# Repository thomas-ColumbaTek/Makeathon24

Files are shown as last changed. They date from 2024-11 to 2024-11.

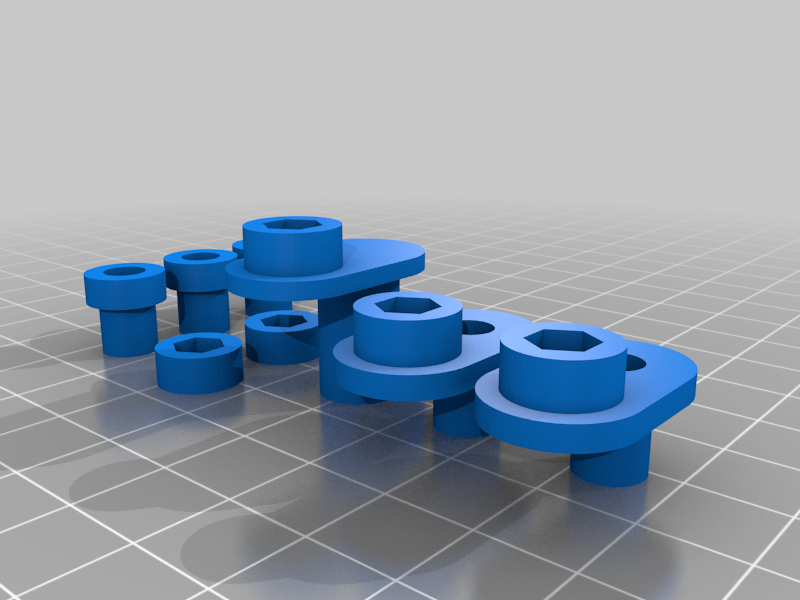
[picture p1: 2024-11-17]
OrbitalShaker/images/835a03b251431fa01c48ba5c81ab6af8.png

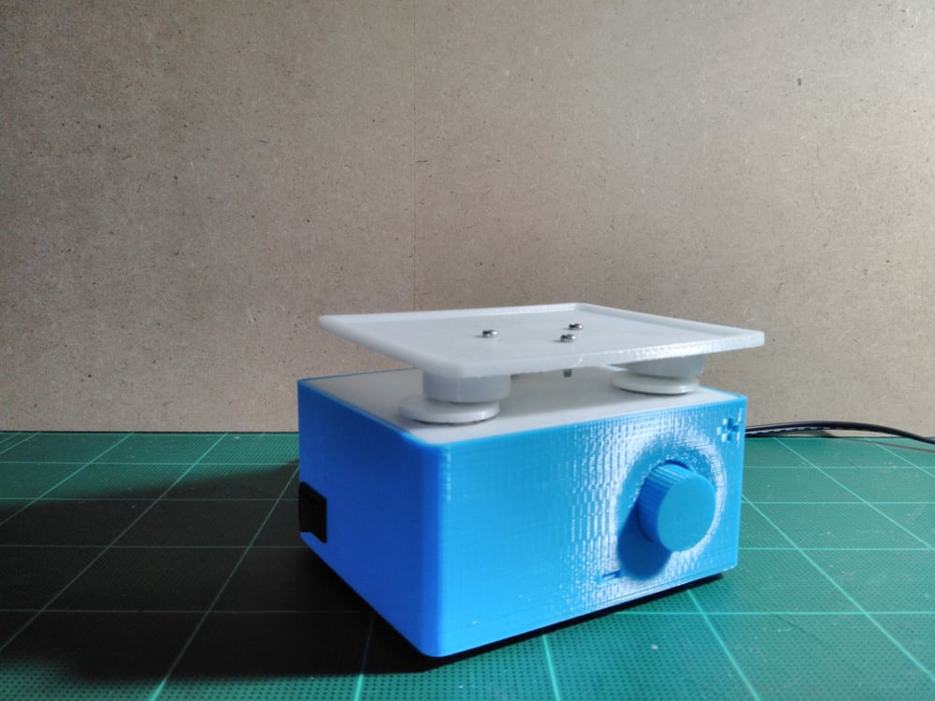
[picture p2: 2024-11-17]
OrbitalShaker/images/IMG_20171108_205839.jpg

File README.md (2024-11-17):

## Welcome to Makeathon2024 Repo

## Orbital Shaker
based on the awesome work:

DIYbio Orbital Shaker V 1.0  by ProgressTH on Thingiverse: https://www.thingiverse.com/thing:2633507

#License
CC BY
DIYbio Orbital Shaker V 1.0
by ProgressTH is licensed under the Creative Commons - Attribution license.

# DIYbio Orbital Shaker V 1.1

Changes:
	- Recreated Linages for usage with heated inserts instead of glued nuts
	- Recreated "Potitower" for better fit and screwed connection to poti and optinal usage of heated inserts
	- Recreated Platform Support with embedded Bearings and inserts
	- Created a Print file for whole Project 
	
## Syringe Pump
based on the awesome work:
Open-Source Syringe Pump by AndreySamokhin - Thingiverse

#License
License CC BY-SA

Open-Source Syringe Pump by AndreySamokhin on Thingiverse: https://www.thingiverse.com/thing:4194094
by AndreySamokhin is licensed under the Creative Commons - Attribution - Share Alike license.

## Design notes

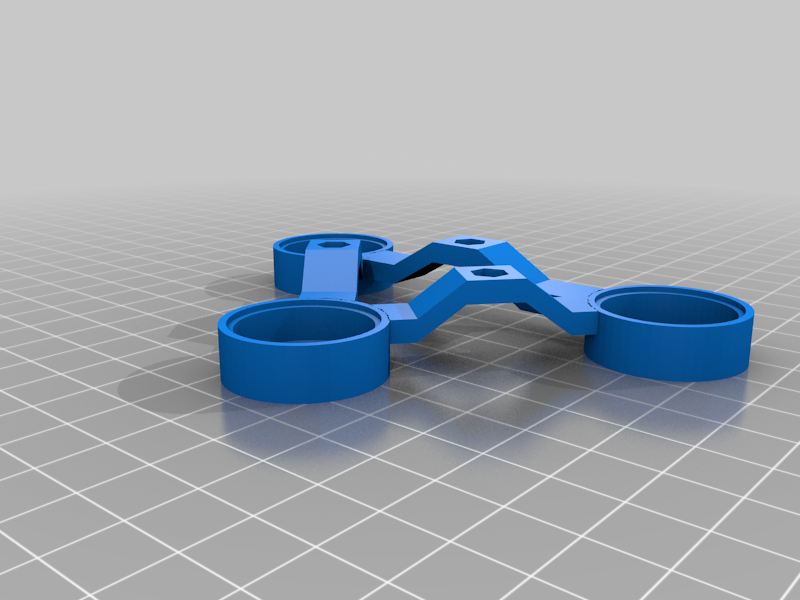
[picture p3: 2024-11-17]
OrbitalShaker/images/801bc46a1355028e08165fc7dd076f1f.png

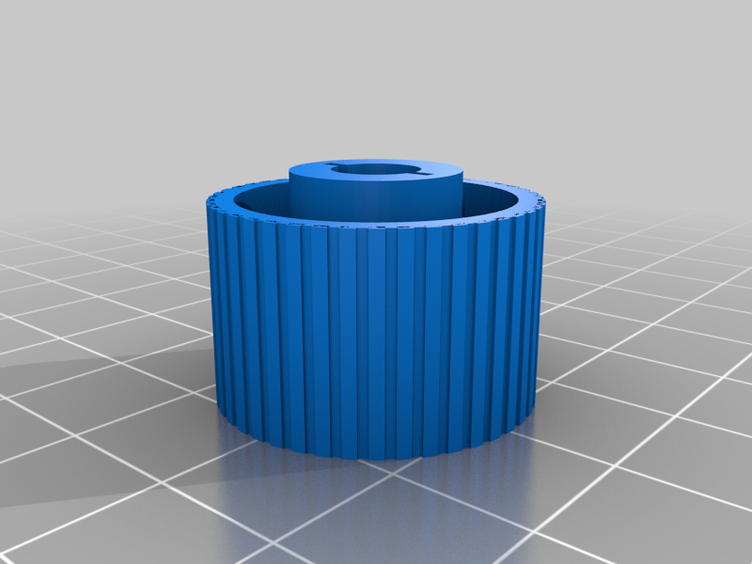
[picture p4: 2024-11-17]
OrbitalShaker/images/b9155d2c6746c89c5fc035d0d0019a35.png

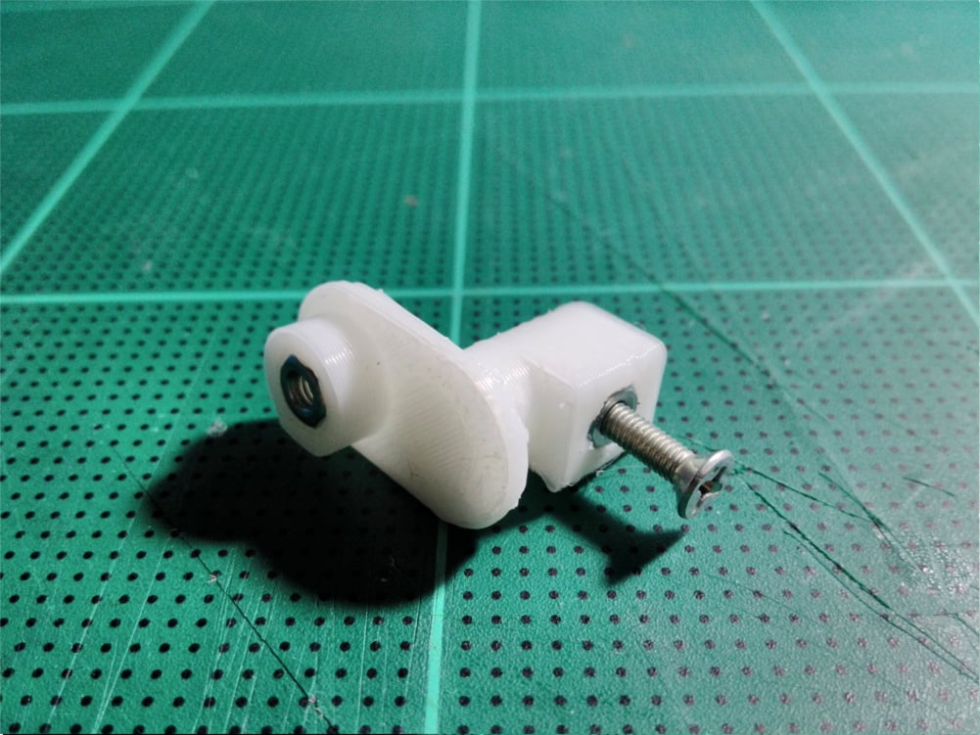
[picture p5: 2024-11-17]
OrbitalShaker/images/StepperCoupling.jpg

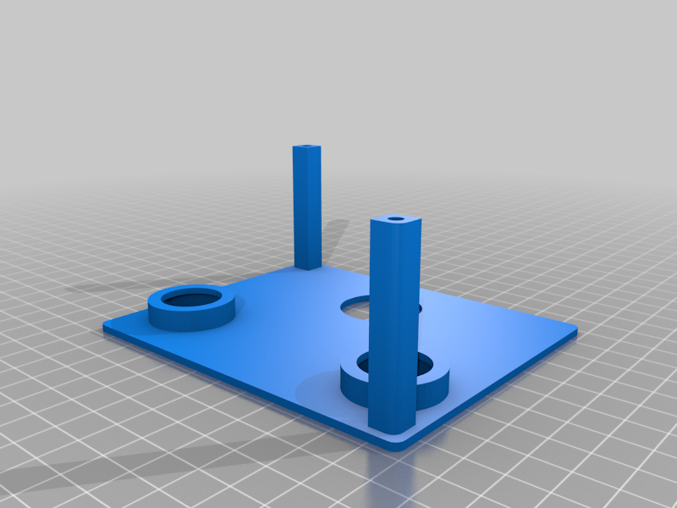
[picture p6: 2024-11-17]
OrbitalShaker/images/b79b12a18a87436c865f9c8a0832d261.png

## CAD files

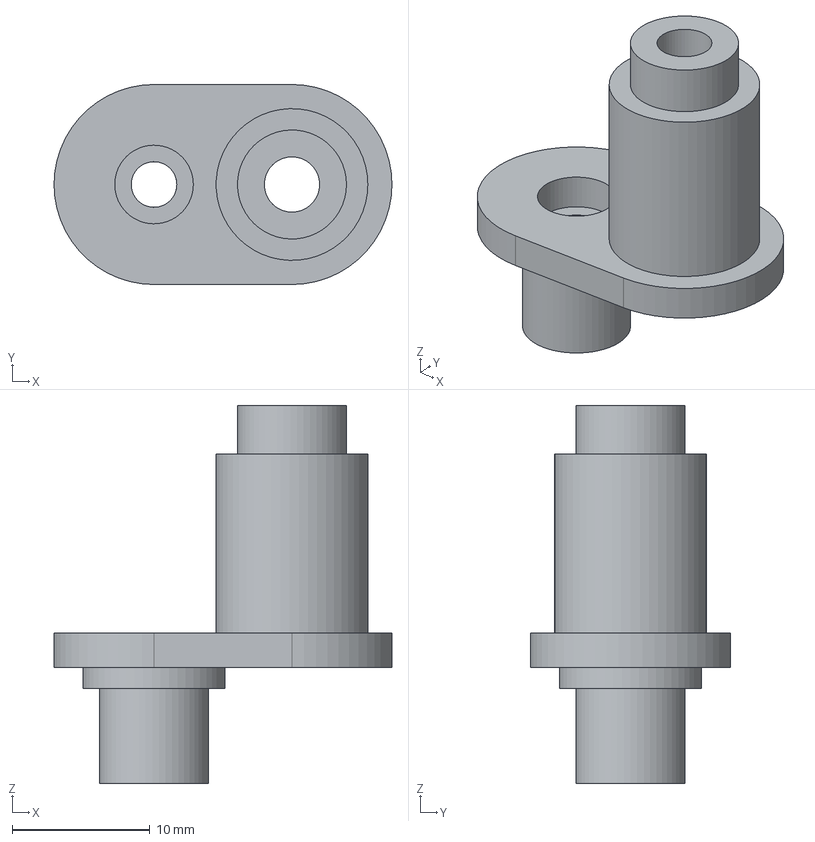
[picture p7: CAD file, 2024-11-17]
OrbitalShaker/Mechanics/linkage-linkage.step
24.5 x 14.5 x 27.4 mm

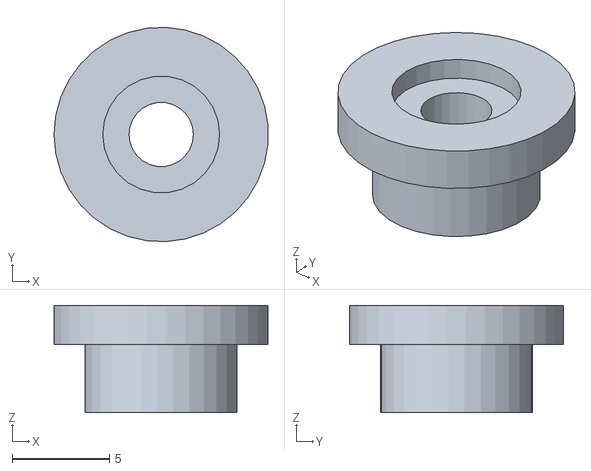
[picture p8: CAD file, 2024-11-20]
OrbitalShaker_Maya_Workshop/insert-insert.obj
11.0 x 11.0 x 5.50

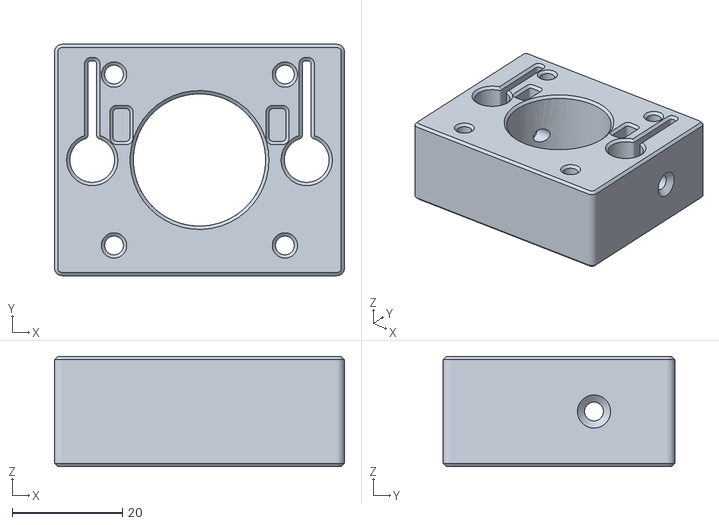
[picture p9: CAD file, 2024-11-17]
SyringePump/Mechanics/backSupport.stl
52.6 x 42.0 x 20.0

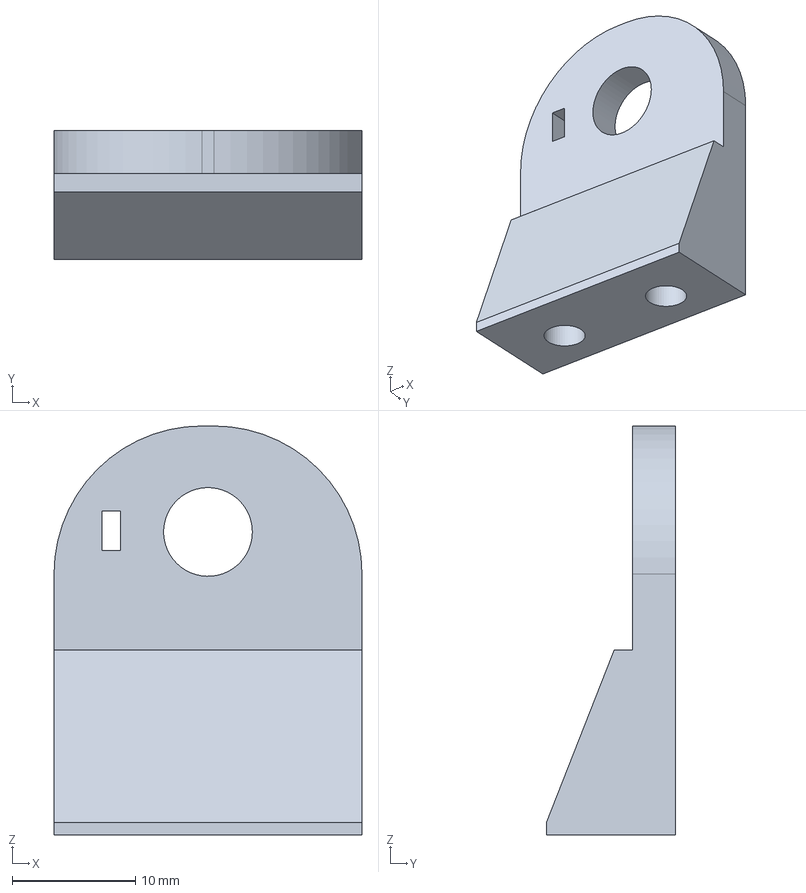
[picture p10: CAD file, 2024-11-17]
OrbitalShaker/Mechanics/PotiTower.FCStd
25.0 x 10.5 x 33.2 mm

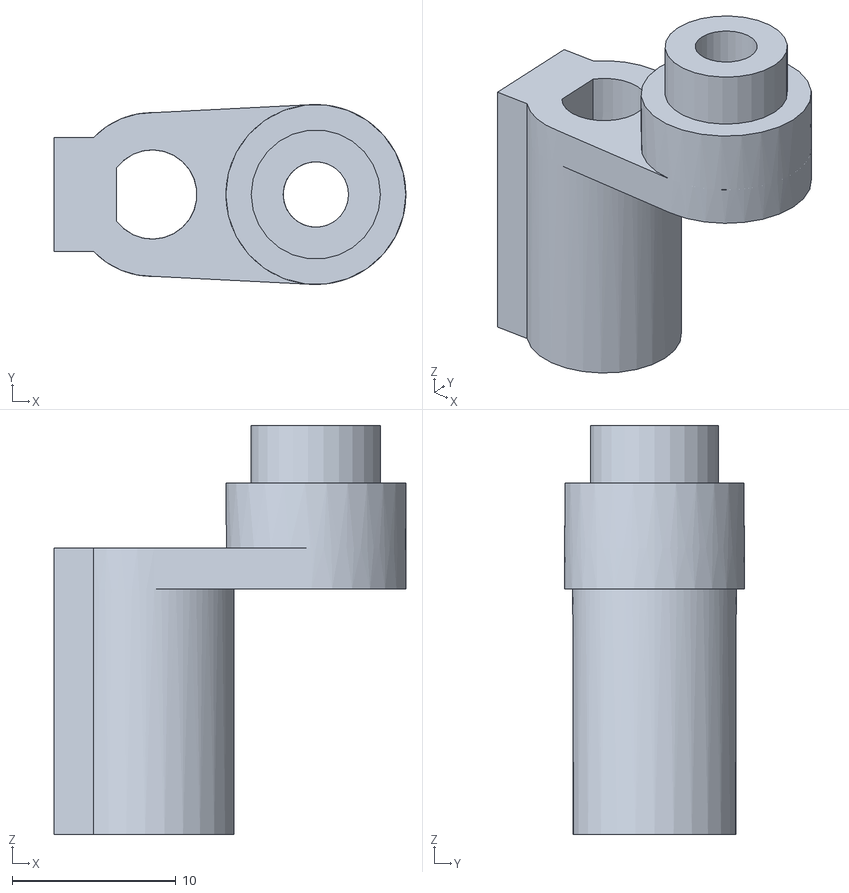
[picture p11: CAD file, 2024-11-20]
OrbitalShaker_Maya_Workshop/linkage2-linkage2.obj
21.5 x 11.0 x 25.0

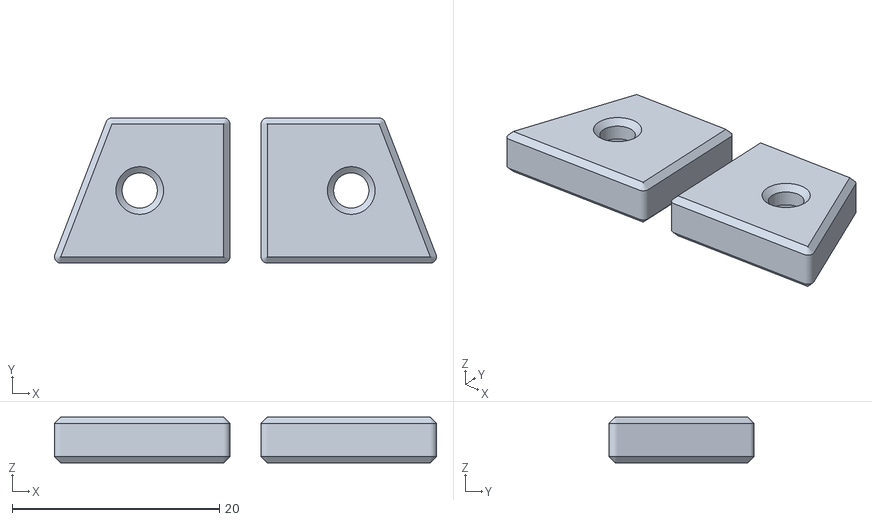
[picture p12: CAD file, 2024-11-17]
SyringePump/Mechanics/plungerHolders.stl
36.8 x 14.0 x 4.40

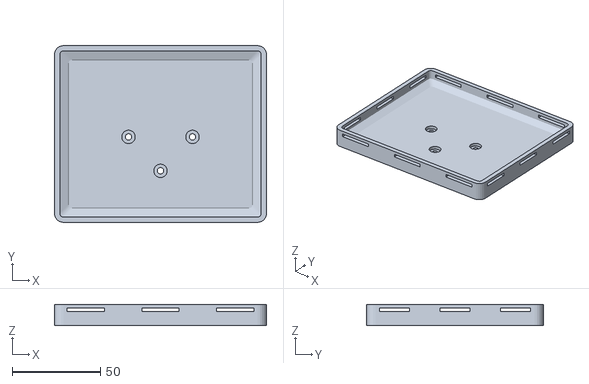
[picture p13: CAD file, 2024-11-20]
OrbitalShaker_Maya_Workshop/Unbenannt3-NewPlatform.obj
120.0 x 100.0 x 12.0

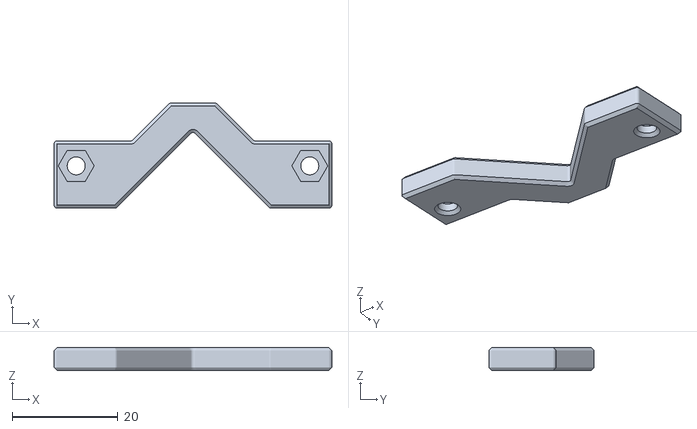
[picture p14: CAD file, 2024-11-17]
SyringePump/Mechanics/sideSyringeHolder.stl
52.6 x 19.9 x 4.40

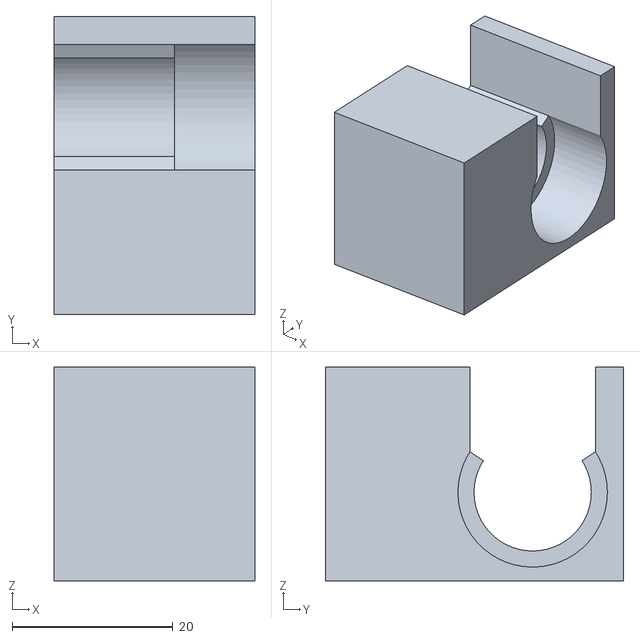
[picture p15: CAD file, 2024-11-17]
OrbitalShaker/Mechanics/Shaker_Potentiometer.stl
25.0 x 37.1 x 26.6

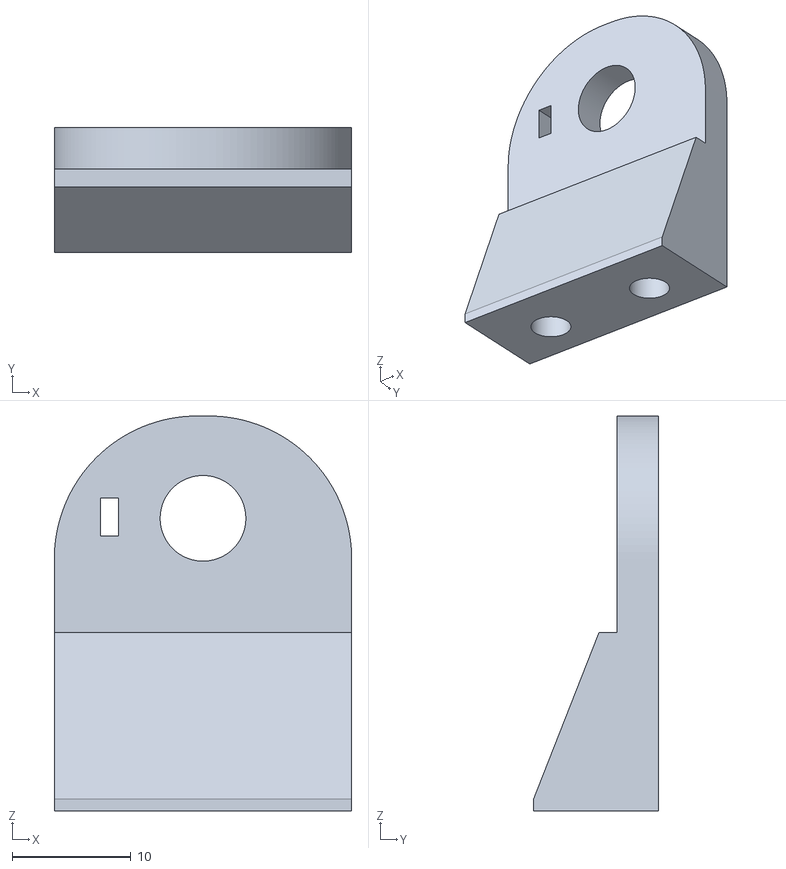
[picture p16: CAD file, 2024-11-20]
OrbitalShaker_Maya_Workshop/PotiTower-Körper.obj
25.0 x 10.5 x 33.2

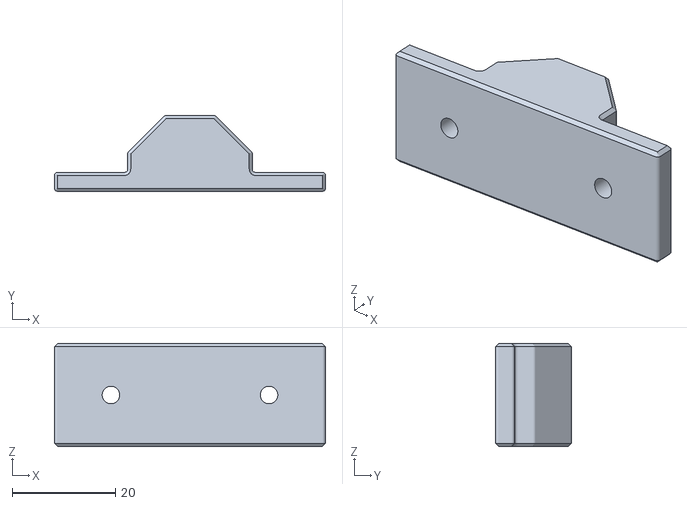
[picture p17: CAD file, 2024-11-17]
SyringePump/Mechanics/topSyringeHolder12mm.stl
52.6 x 14.7 x 20.0

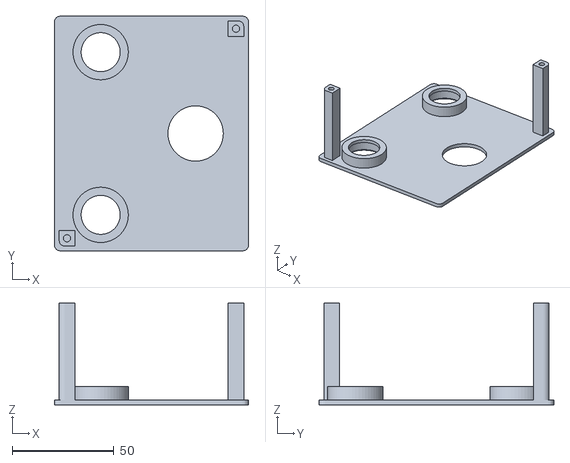
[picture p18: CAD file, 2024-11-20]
OrbitalShaker_Maya_Workshop/Unbenannt1-Shaker_CaseTop.obj
95.4 x 115.4 x 50.0

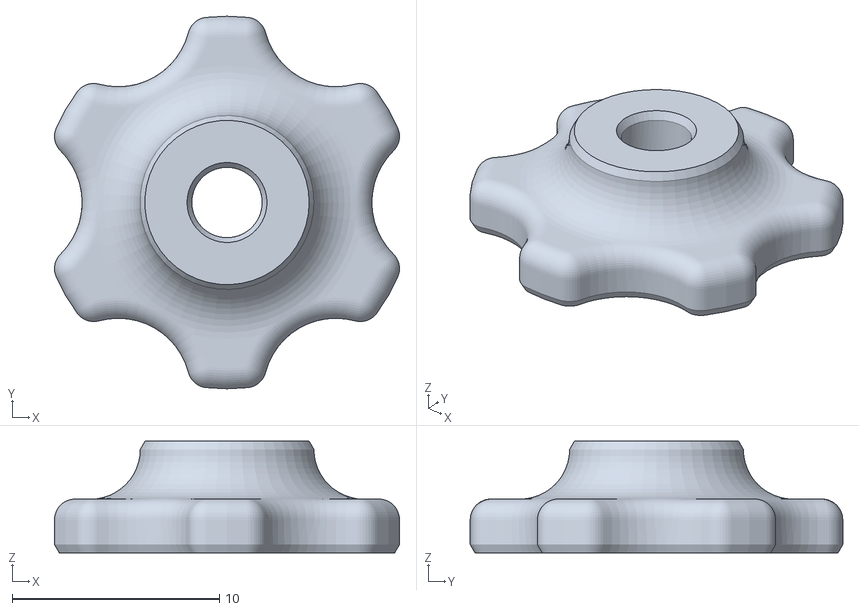
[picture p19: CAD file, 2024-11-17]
SyringePump/Mechanics/handKnob9mm.stl
16.7 x 18.0 x 5.40

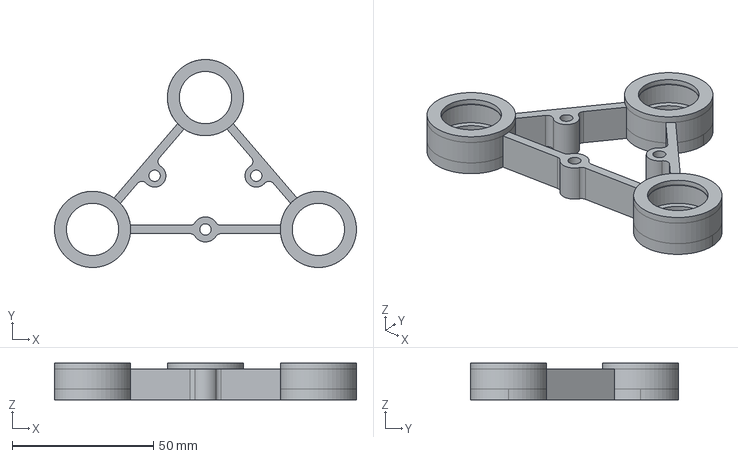
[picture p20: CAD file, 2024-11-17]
OrbitalShaker/Mechanics/PlatformSupport_NEW-support platform.step
107.0 x 73.7 x 13.0 mm

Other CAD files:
OrbitalShaker/Mechanics/linkage2-linkage2.step
OrbitalShaker/Mechanics/insert-insert.step
OrbitalShaker_Maya_Workshop/Shaker_Case.obj
SyringePump/Mechanics/carriage_lm8uu.stl
OrbitalShaker/Mechanics/ControllerPiggyback-Körper001.3mf
OrbitalShaker/Mechanics/ControllerPiggyback.FCStd
OrbitalShaker/Mechanics/OrbitalShaker_all.3mf
OrbitalShaker/Mechanics/PlatformSupport_NEW.FCStd
OrbitalShaker/Mechanics/PotiTower-Körper.3mf
OrbitalShaker/Mechanics/Seeed Studio XIAO-ESP32-C3.step
OrbitalShaker/Mechanics/Shaker.skp
OrbitalShaker/Mechanics/Shaker_Case.stl
OrbitalShaker/Mechanics/Shaker_CaseTop.stl
OrbitalShaker/Mechanics/Shaker_Feet.stl
OrbitalShaker/Mechanics/Shaker_Knob.stl
OrbitalShaker/Mechanics/Shaker_Platform.stl
OrbitalShaker/Mechanics/Washer-washer.step
OrbitalShaker/Mechanics/Washer.FCStd
OrbitalShaker/Mechanics/insert.FCStd
OrbitalShaker/Mechanics/linkage.FCStd
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

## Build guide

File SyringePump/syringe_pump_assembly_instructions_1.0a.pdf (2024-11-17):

# Open-Source Syringe Pump

(developed by Andrey Samokhin in 2018)

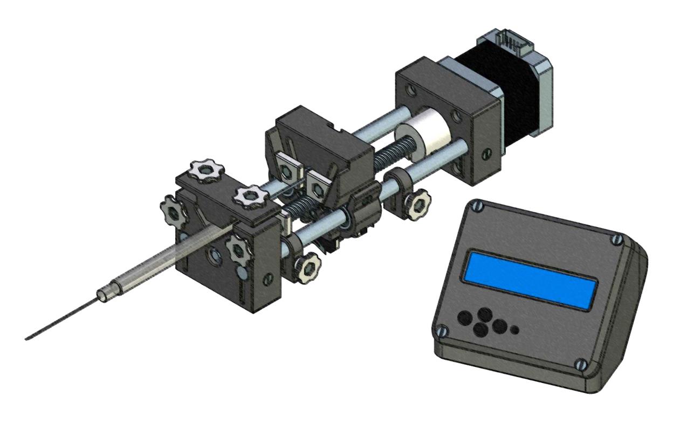
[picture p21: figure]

# Assembly Instructions

(Version 1.0a)

STL-files and "firmware" are available at http://www.mass-spec.ru/projects/diy/syringe_pump/eng/
Project files are distributed under CC BY-SA 4.0 license

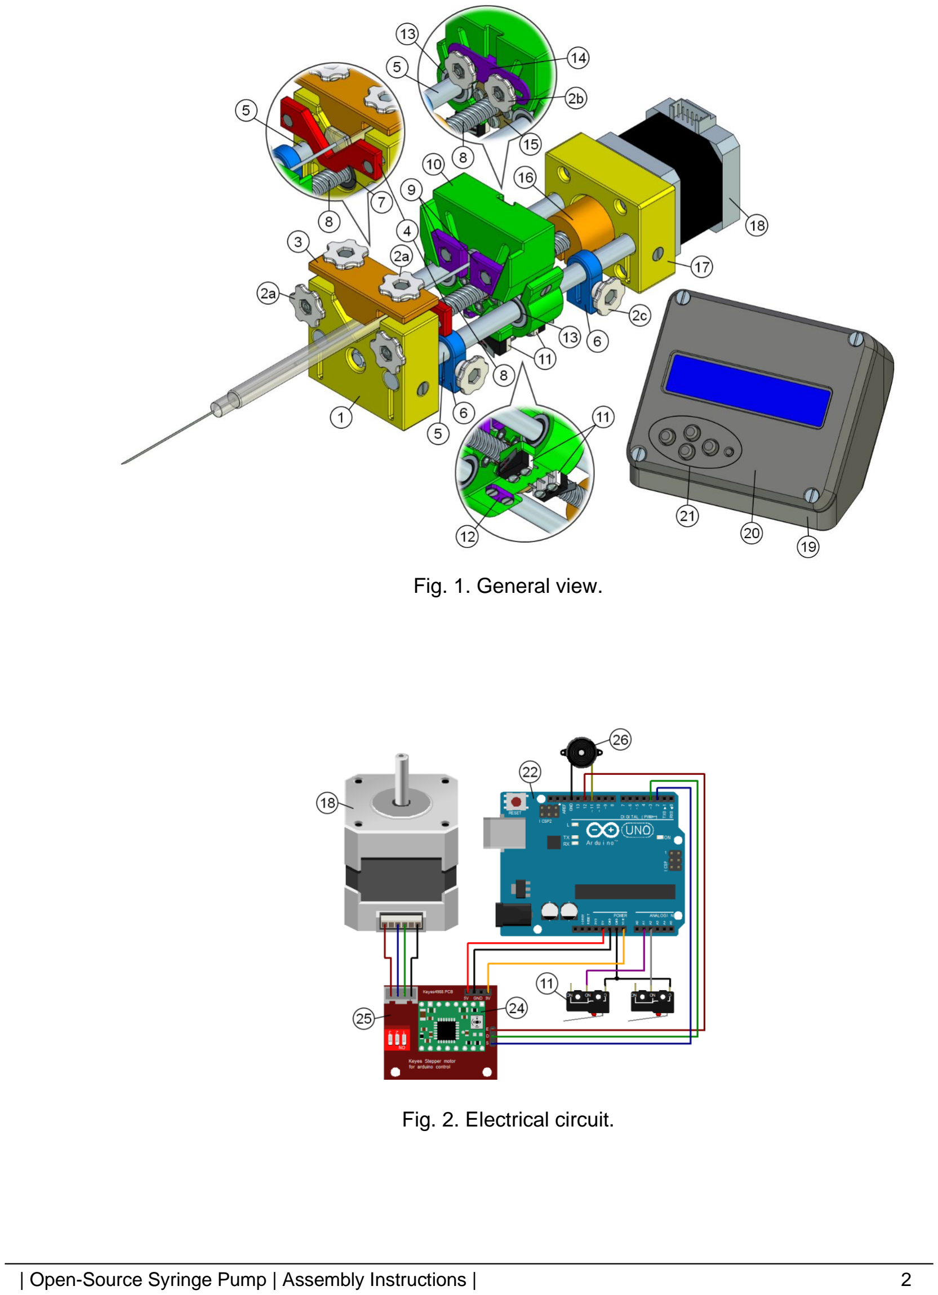
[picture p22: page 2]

| Open-Source Syringe Pump | Assembly Instructions | | 2

Fig. 1. General view.

Fig. 2. Electrical circuit.

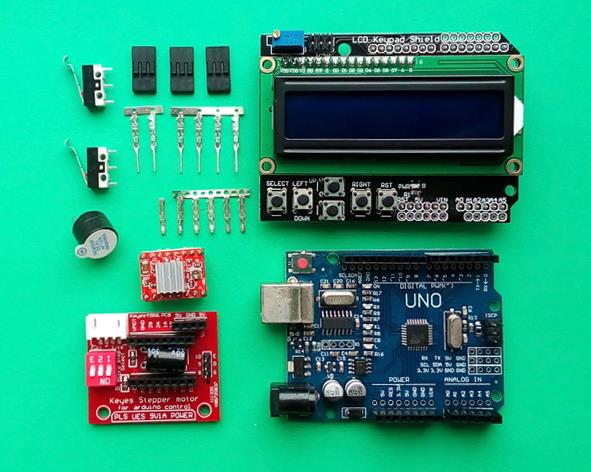
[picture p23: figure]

Fig. 3. Electronic components.

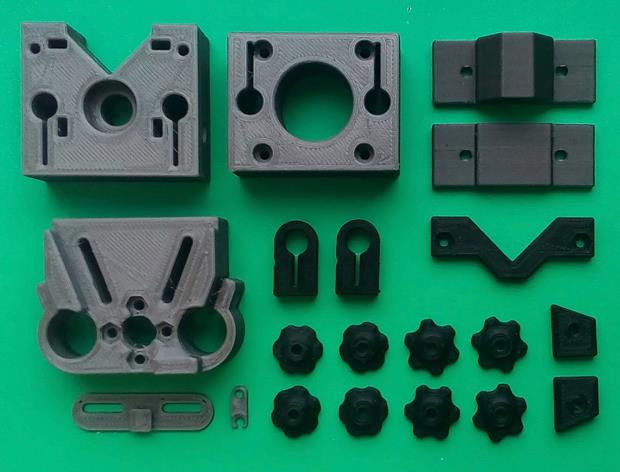
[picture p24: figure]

Fig. 4. Plastic parts made on 3D printer.

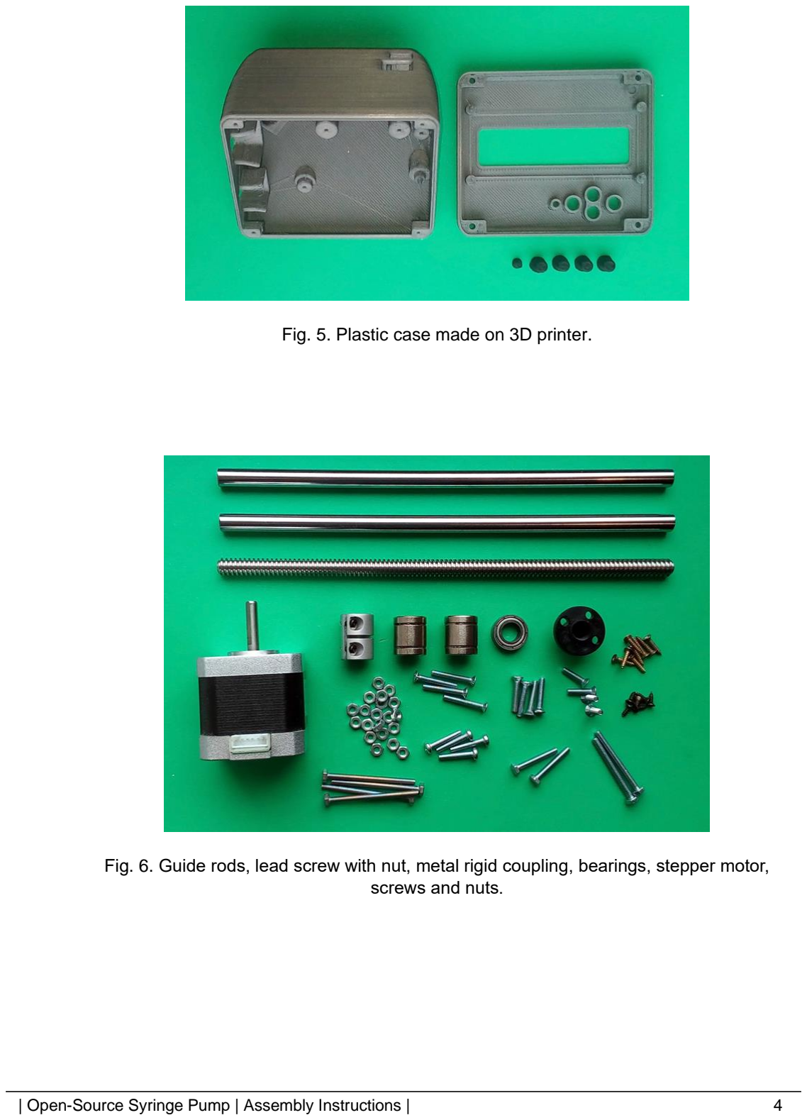
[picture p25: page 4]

Fig. 5. Plastic case made on 3D printer.

Fig. 6. Guide rods, lead screw with nut, metal rigid coupling, bearings, stepper motor, screws and nuts.

| Open

-Source Syringe Pump | Assembly Instructions |
5

Table 1. Part list.

PART # | PART NAME Front Support | QTY 1 1
2a | Hand Knob (9 mm) | 4
2b | Hand Knob (8 mm) | 2
2c | Hand Knob (7 mm) | 2
3 | Top Syringe Holder | 1
4 | Side Syringe Holder | 1
5 | Guide Rod (D=8 mm) | 2
6 | Limit Stop | 2
7 | Bearing 688ZZ | 1
8 | Lead Screw (T8) | 1
9 | Plunger Holders | 1
10 | Carriage | 1
11 | Endstop Switch | 2
12 | Wire Holder | 1
13 | Linear Bearing (LM8SUU) | 2
14 | Slider | 1
15 | Lead Screw Nut (T8) | 1
16 | Coupling | 1
17 | Back Support | 1
18 | Stepper Motor (NEMA 17) | 1
19 | Case (Base ) | 1
20 | Case (Cover ) | 1
21 | Buttons | 1
22 | Arduino UNO | 1
23 | LCD Keypad Shield | 1
24 | Stepper Motor Driver (A4988) | 1
25 | Control Shield for A4988 | 1
26 | Active Buzzer (D=12 mm) | 1
27 | Nut M3 | 20
28 | Countersunk Screw M3x12 | 4
29 | Countersunk Screw M3x14 | 4
30 | Countersunk Screw M3x20 | 4
31 | Pan Head Screw M3x16 | 4
32 | Bolt M3x20 | 2
33 | Bolt M3x25 | 2
34 | Bolt M3x35 | 4
35 | Self -tapping Screw 2x8 | 6
36 | Self -tapping Screw 2x10 | 8
37 | Dupont Connector (Female) | 6
38 | Dupont Connector (Male) | 6
39 | Dupont Housing (3P) | 3
40 | Connector Wires | –
41 | Power Supply (12 V, 2 A) | 1

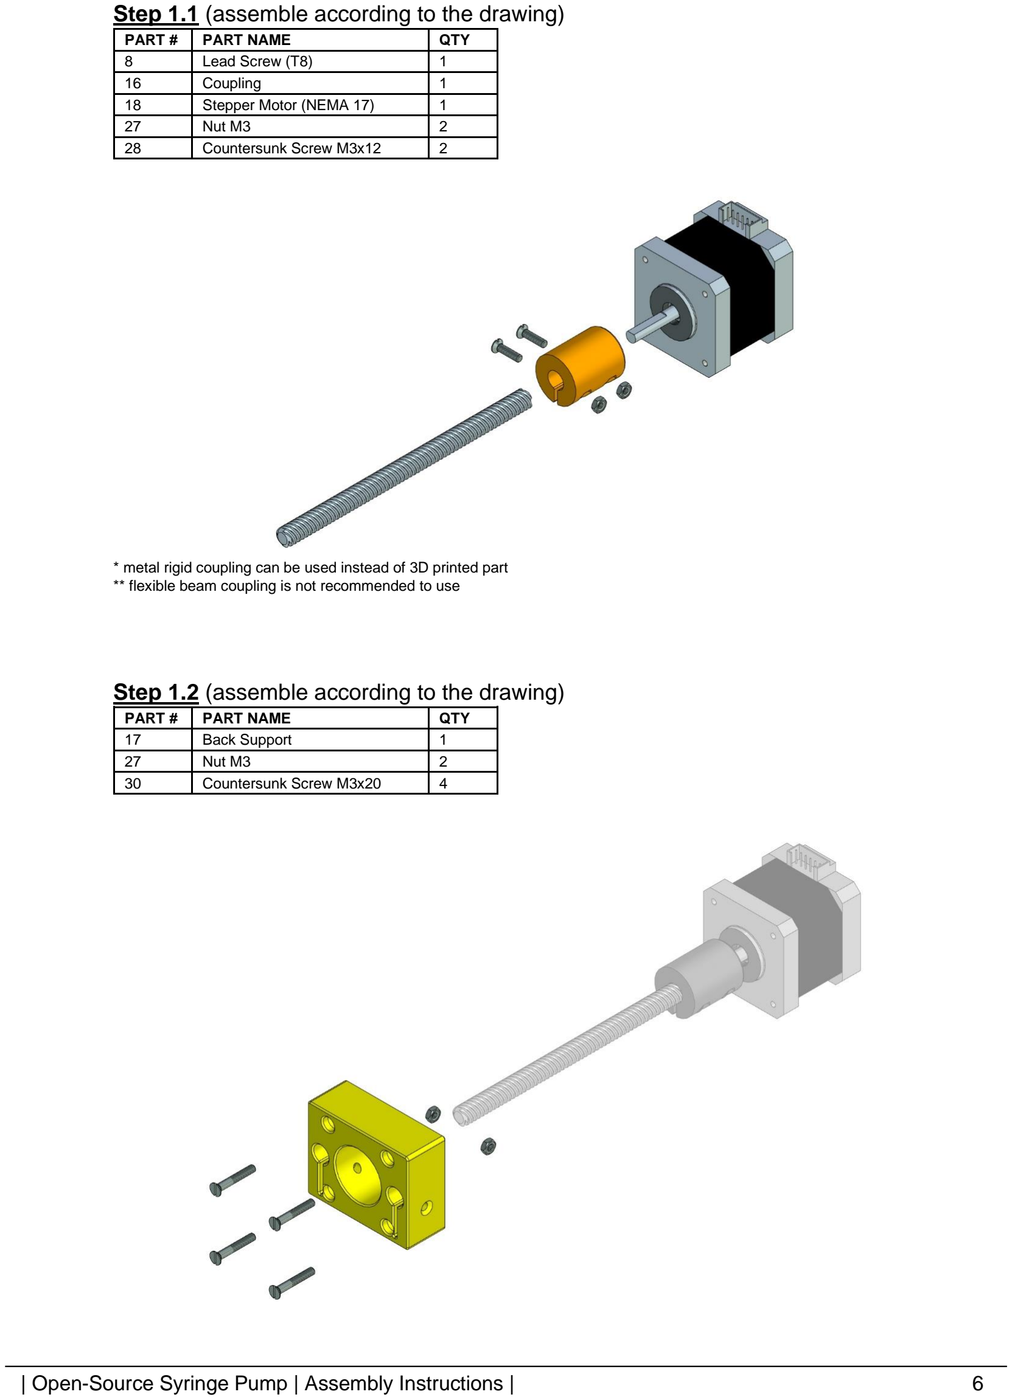
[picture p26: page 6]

Step 1.1 (assemble according to the drawing)
PART # | PART NAME | QTY
8 | Lead Screw (T8) | 1
16 | Coupling | 1
18 | Stepper Motor (NEMA 17) | 1
27 | Nut M3 | 2
28 | Countersunk Screw M3x12 | 2

* metal rigid coupling can be used instead of 3D printed part ** flexible beam coupling is not recommended to use

Step 1.2 (assemble according to the drawing)
PART # | PART NAME | QTY
17 | Back Support | 1
27 | Nut M3 | 2
30 | Countersunk Screw M3x20 | 4

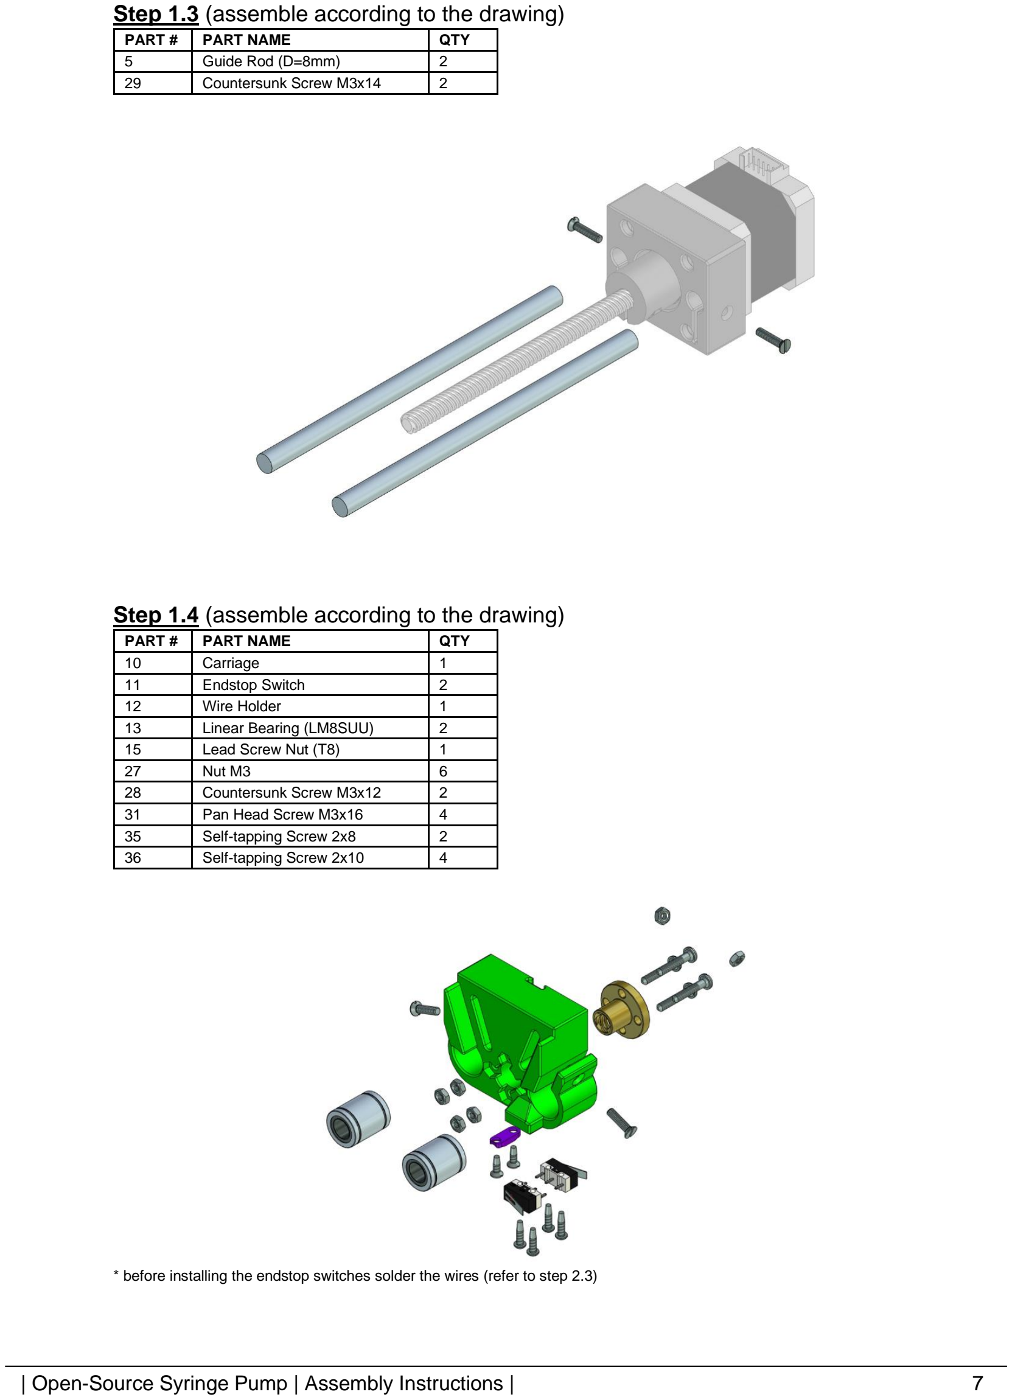
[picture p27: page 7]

Step 1.3 (assemble according to the drawing)
PART # | PART NAME | QTY
5 | Guide Rod (D=8mm) | 2
29 | Countersunk Screw M3x14 | 2
Step 1.4 (assemble according to the drawing)
PART # | PART NAME | QTY
10 | Carriage | 1
11 | Endstop Switch | 2
12 | Wire Holder | 1
13 | Linear Bearing (LM8SUU) | 2
15 | Lead Screw Nut (T8) | 1
27 | Nut M3 | 6
28 | Countersunk Screw M3x12 | 2
31 | Pan Head Screw M3x16 | 4
35 | Self-tapping Screw 2x8 | 2
36 | Self-tapping Screw 2x10 | 4

* before installing the endstop switches solder the wires (refer to step 2.3)

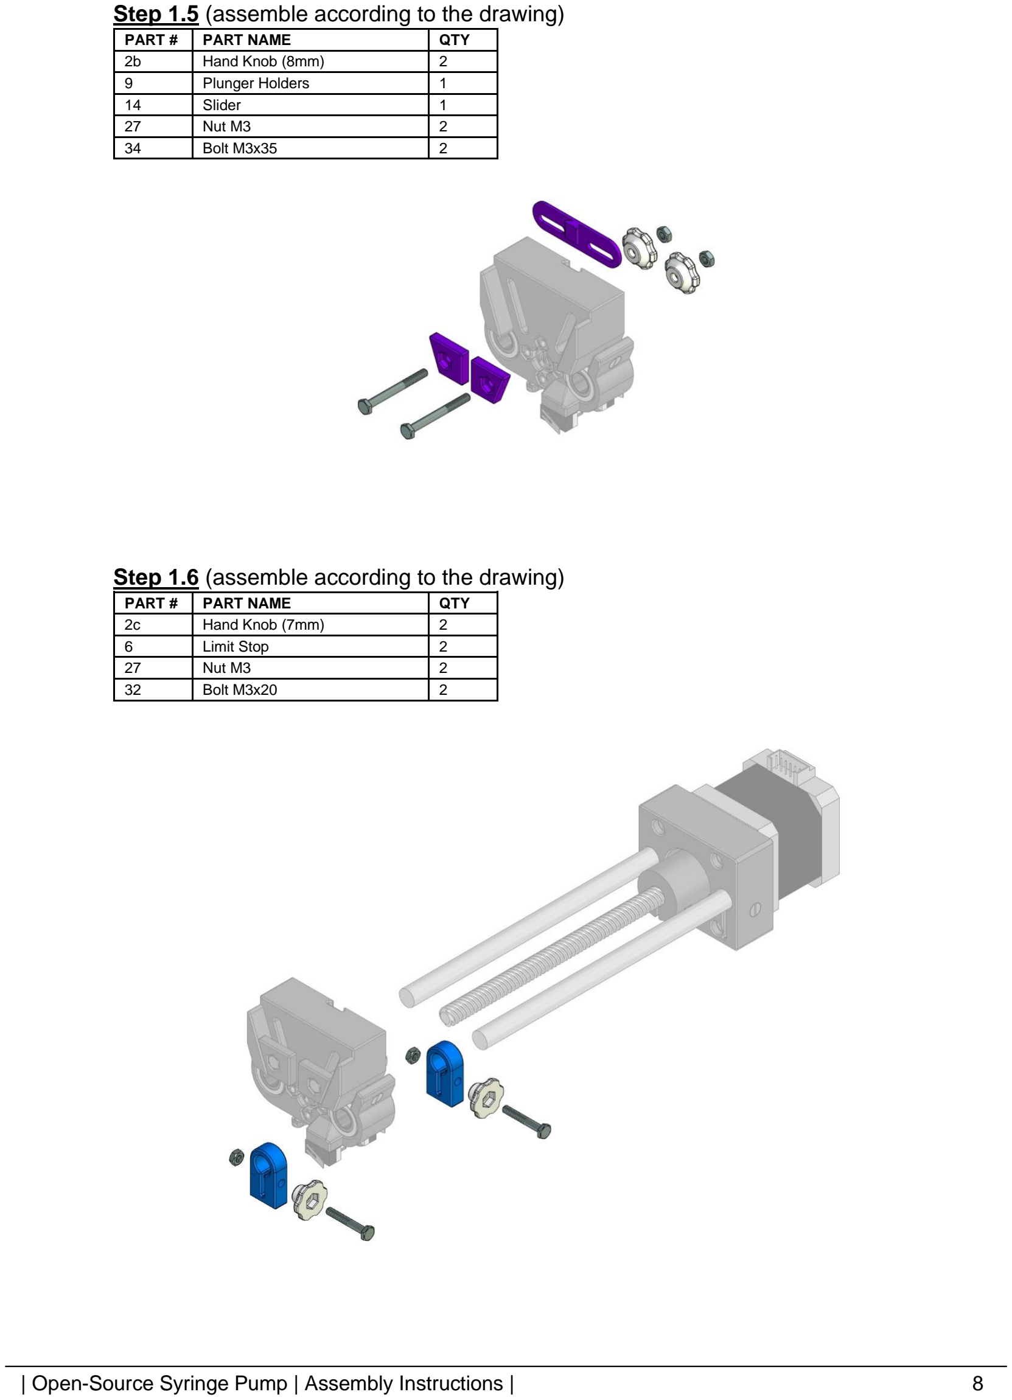
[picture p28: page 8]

Step 1.5 (assemble according to the drawing)
PART # | PART NAME | QTY
2b | Hand Knob (8mm) | 2
9 | Plunger Holders | 1
14 | Slider | 1
27 | Nut M3 | 2
34 | Bolt M3x35 | 2
Step 1.6 (assemble according to the drawing)
PART # | PART NAME | QTY
2c | Hand Knob (7mm) | 2
6 | Limit Stop | 2
27 | Nut M3 | 2
32 | Bolt M3x20 | 2

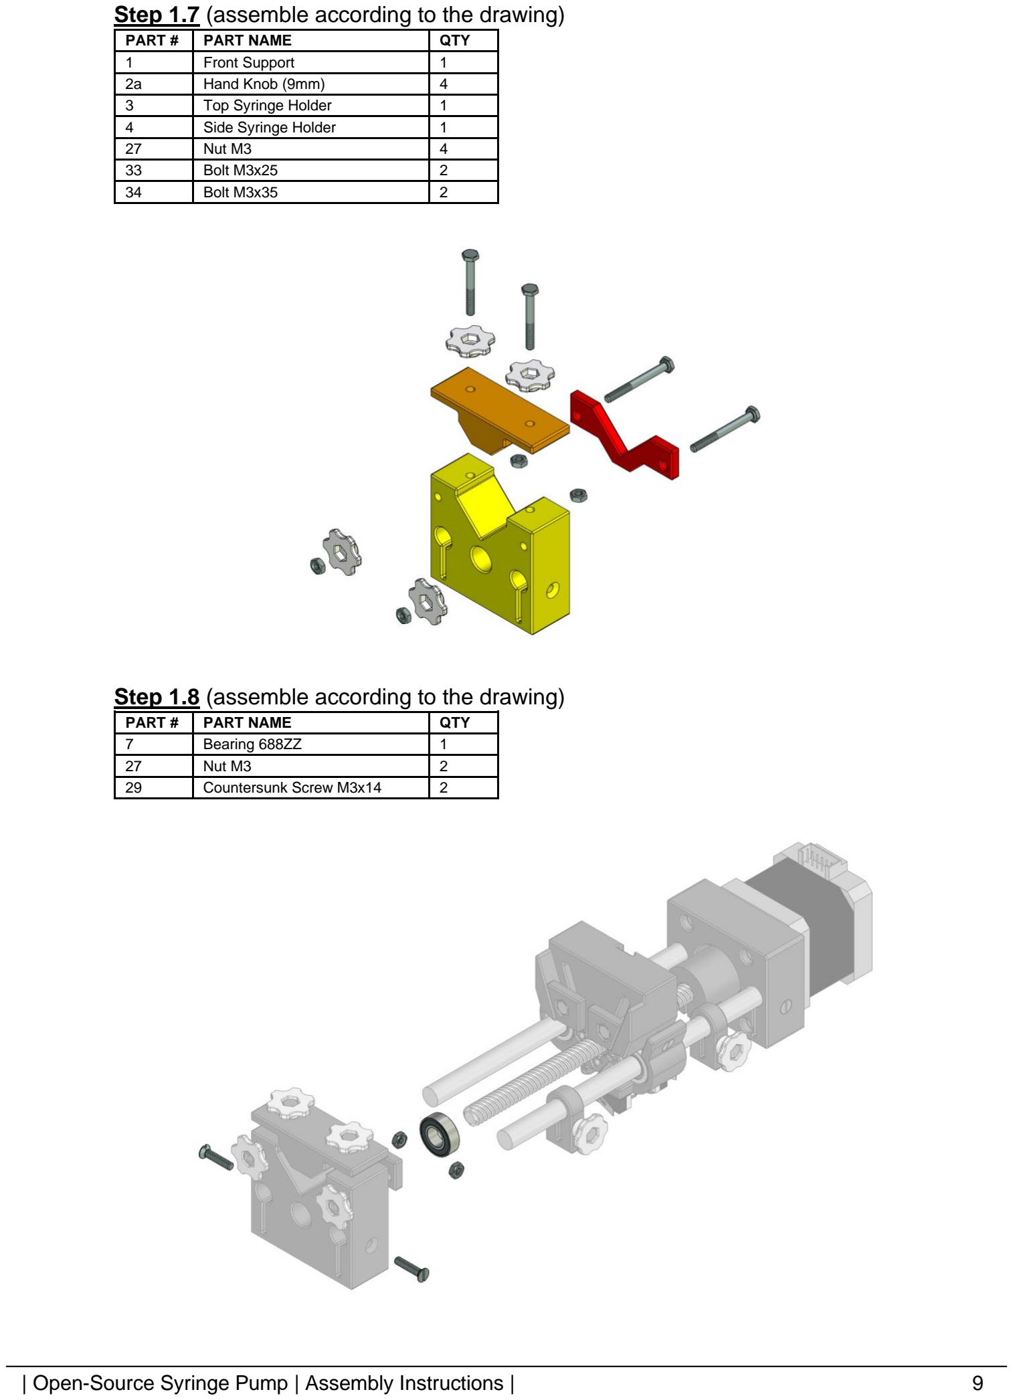
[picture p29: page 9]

Step 1.7 (assemble according to the drawing)
PART # | PART NAME | QTY
1 | Front Support | 1
2a | Hand Knob (9mm) | 4
3 | Top Syringe Holder | 1
4 | Side Syringe Holder | 1
27 | Nut M3 | 4
33 | Bolt M3x25 | 2
34 | Bolt M3x35 | 2
Step 1.8 (assemble according to the drawing)
PART # | PART NAME | QTY
7 | Bearing 688ZZ | 1
27 | Nut M3 | 2
29 | Countersunk Screw M3x14 | 2

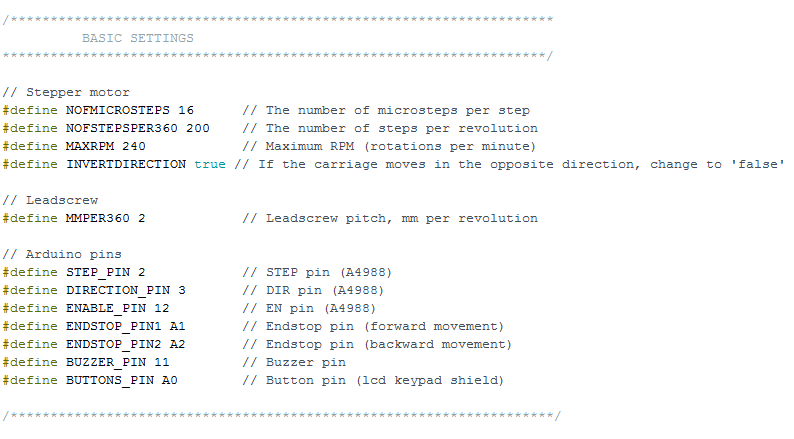
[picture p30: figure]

Step 2.1 (if necessary, change the basic settings in the Arduino sketch)
Step 2.2 (upload sketch to Arduino) Detailed instructions are available at this link. (https://www.arduino.cc/en/main/howto)
Step 2.3 (solder wires and crimp connectors, refer to electrical circuit)
PART # | PART NAME | QTY
22 | Arduino UNO | 1
26 | Active Buzzer (D=12mm) | 1
37 | Dupont Connector (Female) | 6
38 | Dupont Connector (Male) | 3
39 | Dupont Housing (3P) | 2
40 | Connector Wires | –

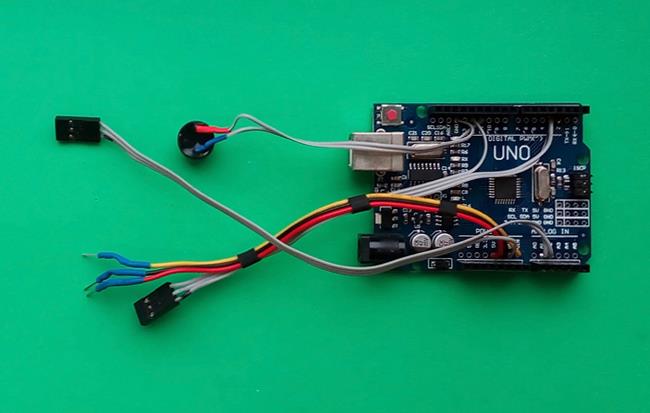
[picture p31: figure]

Step 2.4 (solder wires and crimp connectors, refer to electrical circuit)
PART # | PART NAME | QTY
11 | Endstop Switch | 2
38 | Dupont Connector (Male) | 3
39 | Dupont Housing (3P) | 1
40 | Connector Wires | –

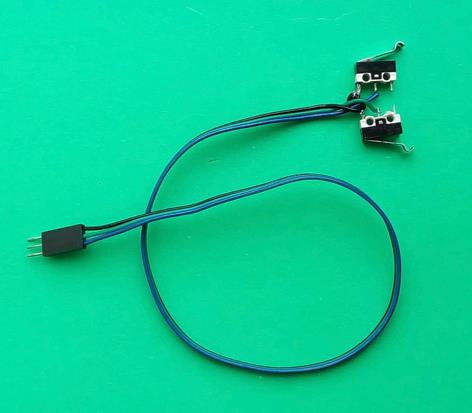
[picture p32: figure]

Step 2.5 (plug A4988 driver into the shield and set all DIP switches to ON)
PART # | PART NAME | QTY
24 | Stepper Motor Driver (A4988) | 1
25 | Control Shield for A4988 | 1

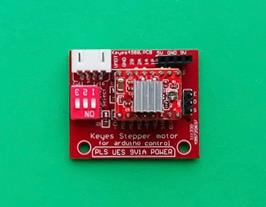
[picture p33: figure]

Step 2.6 (set output current limit on A4988) Detailed instructions are available at this link. (https://howtomechatronics.com/tutorials/arduino/how-to-control-stepper-motor-with-a4988-driver-and-arduino/)

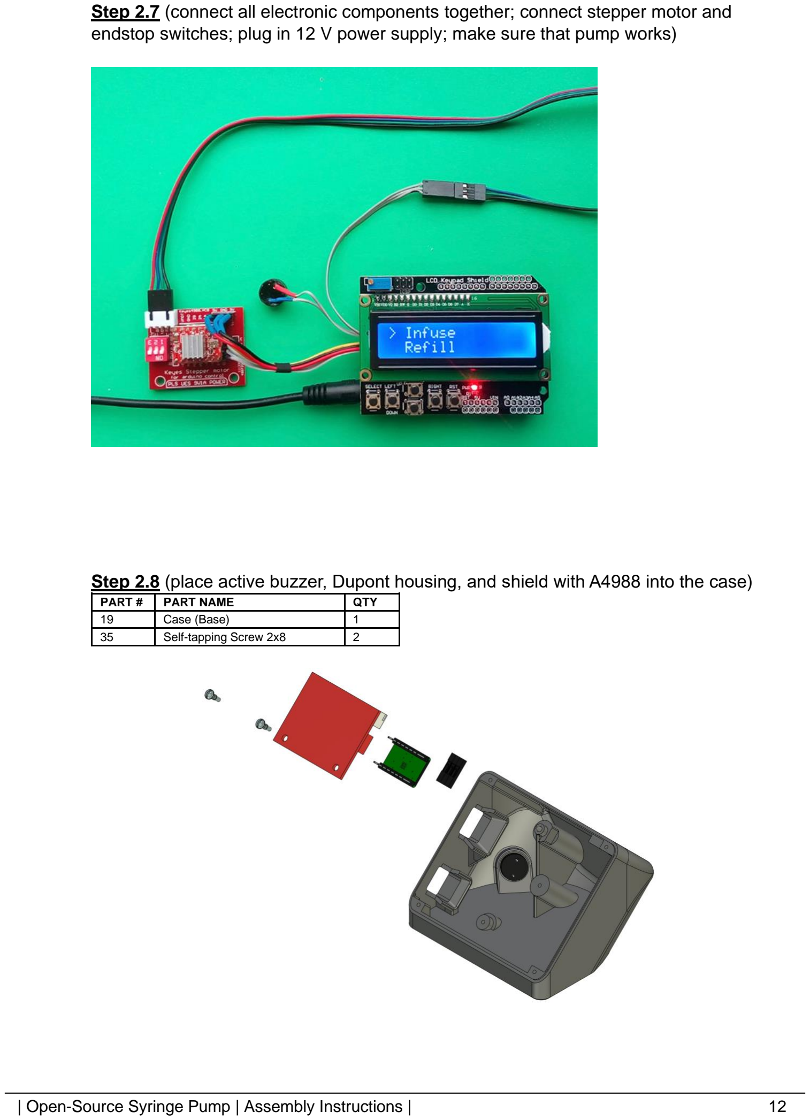
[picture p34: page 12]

Step 2.7 (connect all electronic components together; connect stepper motor and endstop switches; plug in 12 V power supply; make sure that pump works)
Step 2.8 (place active buzzer, Dupont housing, and shield with A4988 into the case)
PART # | PART NAME | QTY
19 | Case (Base) | 1
35 | Self-tapping Screw 2x8 | 2

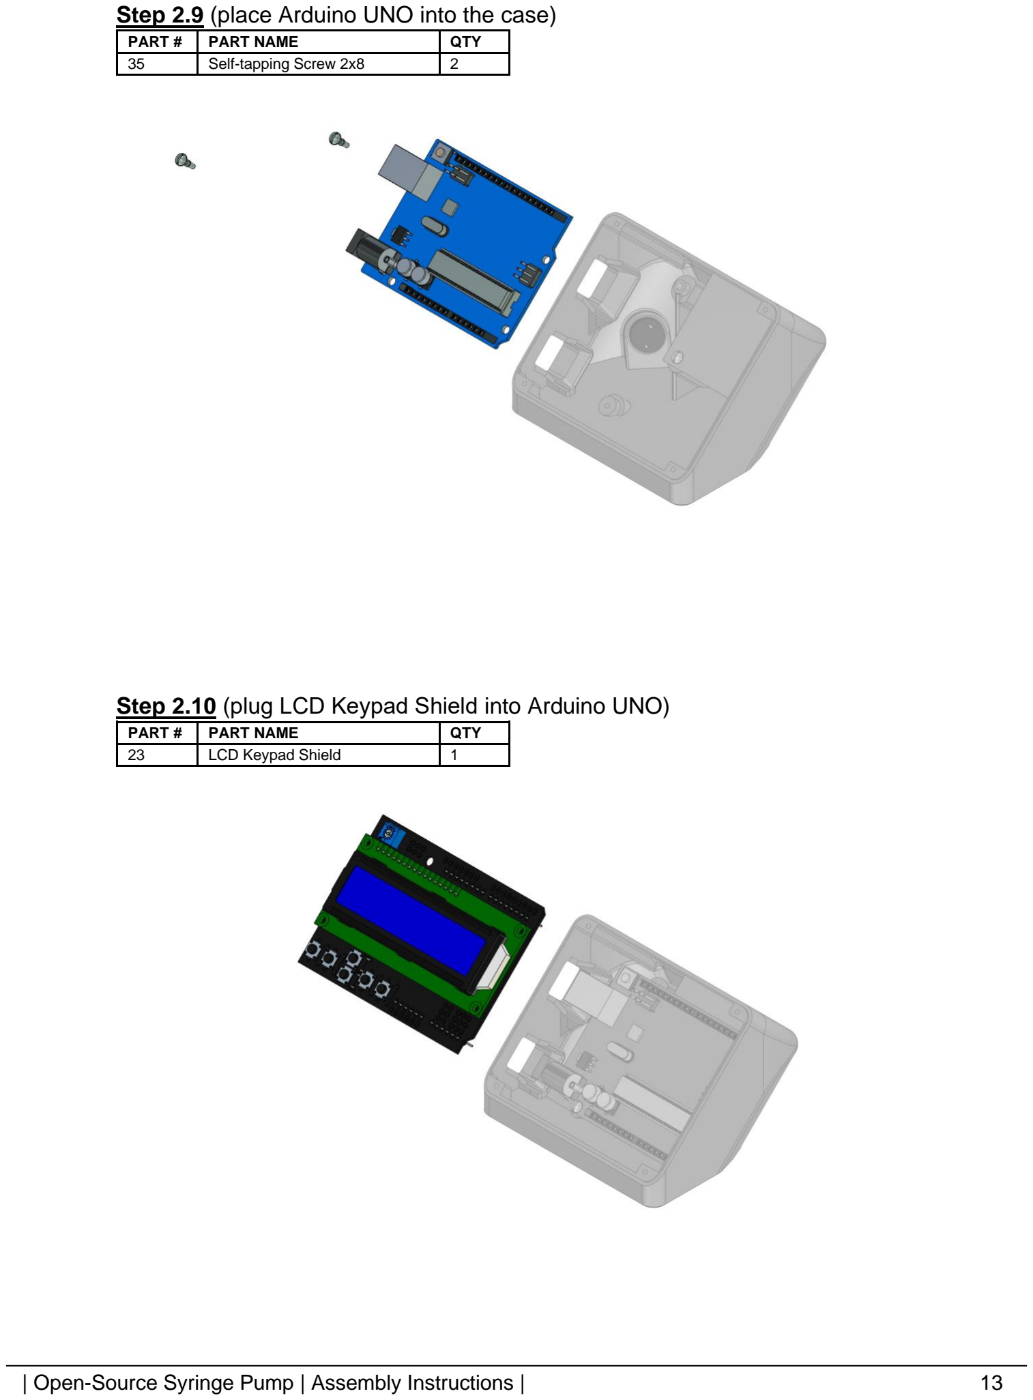
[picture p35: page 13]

Step 2.9 (place Arduino UNO into the case)
PART # | PART NAME | QTY
35 | Self-tapping Screw 2x8 | 2
Step 2.10 (plug LCD Keypad Shield into Arduino UNO)
PART # | PART NAME | QTY
23 | LCD Keypad Shield | 1

Step 2.11 (install buttons and top cover)
PART # | PART NAME | QTY
20 | Case (Cover) | 1
21 | Buttons | 1
36 | Self-tapping Screw 2x10 | 4

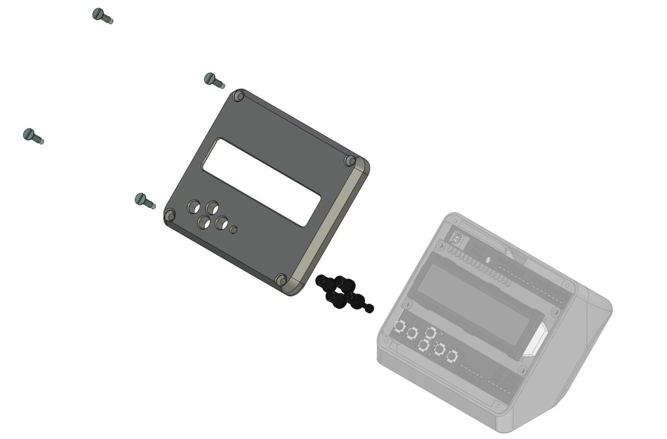
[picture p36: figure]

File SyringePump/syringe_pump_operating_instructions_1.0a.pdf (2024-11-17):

# Open-Source Syringe Pump

(developed by Andrey Samokhin in 2018)


# Operating Instructions

(Version 1.0a)

STL-files and "firmware" are available at http://www.mass-spec.ru/projects/diy/syringe_pump/eng/
Project files are distributed under CC BY-SA 4.0 license

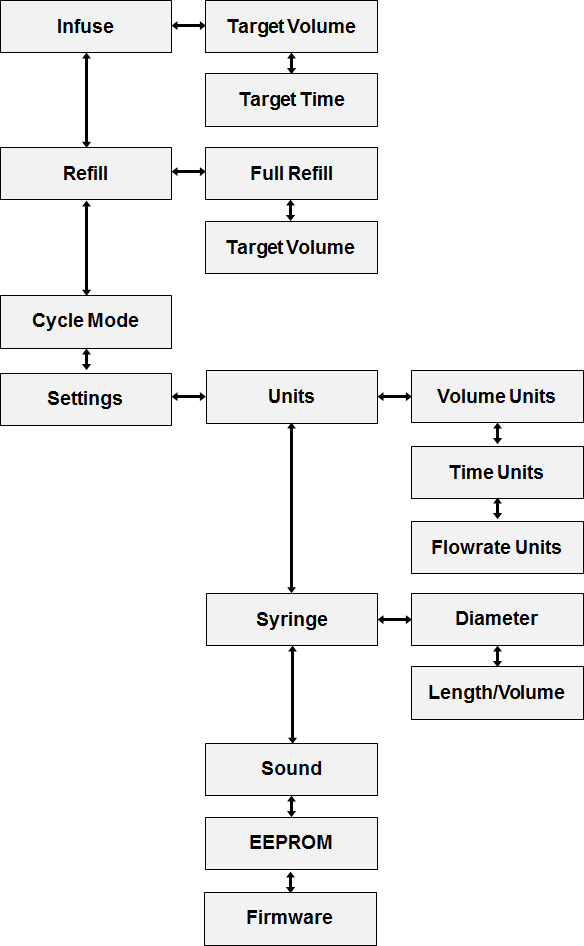
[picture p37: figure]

| Open-Source Syringe Pump | Operating Instructions | | 2

Navigation
Press ▲ or ▼ button to select a menu item.
Press ► button to enter submenu or to perform/confirm action. Press ◄ button to go back or to cancel action.

Fig. 1. Control buttons

Changing value
Press ▼ button to enter setting mode.
Press (or hold) ► or ◄ button to select a digit.
Press (or hold) ▲ or ▼ button to modify selected digit.
To confirm change press ► button several times until you exit setting mode. To cancel change press ◄ button several times until you exit setting mode.

Fig. 2. Menu structure

Left

Right
Down

Up

Reset

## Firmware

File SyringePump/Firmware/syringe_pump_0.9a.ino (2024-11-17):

#include <LiquidCrystal.h>
#include <EEPROM.h>



/********************************************************************
          BASIC SETTINGS
********************************************************************/

// Stepper motor
#define NOFMICROSTEPS 16      // The number of microsteps per step
#define NOFSTEPSPER360 200    // The number of steps per revolution
#define MAXRPM 240            // Maximum RPM (rotations per minute)
#define INVERTDIRECTION true // If the carriage moves in the opposite direction, change to 'false'

// Leadscrew
#define MMPER360 2            // Leadscrew pitch, mm per revolution

// Arduino pins
#define STEP_PIN 2            // STEP pin (A4988)
#define DIRECTION_PIN 3       // DIR pin (A4988)
#define ENABLE_PIN 12         // EN pin (A4988)
#define ENDSTOP_PIN1 A1       // Endstop pin (forward movement)
#define ENDSTOP_PIN2 A2       // Endstop pin (backward movement)
#define BUZZER_PIN 11         // Buzzer pin
#define BUTTONS_PIN A0        // Button pin (lcd keypad shield)

/********************************************************************/



#define DEBOUNCEDELAY 50
#define LONGPRESSDELAY 450
#define AUTOCHANGINGDELAY 300

#define NITEMS 43

#define LINK2S 12
#define LINK2E 13
#define LINK2V 20
#define LINK2T 21
#define LINK2F 22
#define LINK2DIA 41
#define LINK2LPV 42

LiquidCrystal lcd(8, 9, 4, 5, 6, 7);

struct MenuItem
{
  uint8_t button[4];
  uint8_t type;
  char *text;
  uint8_t address;
  uint32_t value;
};

enum listOfButtons {RIGHT, UP, DOWN, LEFT, SELECT, NA};
enum listOfButtonStates {RELEASE, SHORTPRESS, MEDIUMPRESS, LONGPRESS};
enum listOfPrograms {CHANGEVALUE = 200, SELECTFROMLIST, INFUSEVOLUME, INFUSETIME, REFILLVOLUME, REFILLFULL, CYCLEMODE, FIRMWAREINFO};
enum listOfItemTypes {TEXT, LIST, VOLUME, TIME, FLOWRATE, LENGTHPERVOLUME, DIAMETER};

const char firmwareInfo[] = "0.9a";
const uint16_t volumeDivider[2] = {1000, 1};
const uint16_t timeDivider[3] = {1, 60, 3600};
const uint16_t flowrateDivider[4] = {60000, 1000, 60, 1};
const float stepsPERmm = NOFSTEPSPER360 / MMPER360;

MenuItem items[NITEMS];
uint8_t lastButton = NA;
uint8_t buttonState = RELEASE;
uint32_t buttonPressTime = 0;
uint8_t currentItem = 1;
float coef;
uint8_t endStopPin;
volatile uint32_t ustepCounter;
uint32_t ustepCounterLimit;

uint32_t getValue(uint8_t itemNo);
void changeValue();
void setValue(uint8_t itemNo, uint8_t digits[8]);
void selectFromList();
void calculateActualValue(uint8_t itemNo);
void recalculateSyringe(uint8_t itemNo);
void printScreen();
void printUnits();
void printFirmwareInfo();
void printTimeAndVolume(uint16_t pumpingTime, uint32_t pumpingVolume);
void showScreensaver();
void readFromEEPROM(uint8_t itemNo);
void writeToEEPROM(uint8_t itemNo);
void getButtonState();
uint16_t valueDivider (uint8_t n);
uint8_t getElementNo(uint8_t linkToList);
void waitingForButton(uint8_t buttonCode, uint8_t itemNo);
void beep (uint16_t delayOn = 15, uint16_t delayOff = 100);
bool checkEndstop(int8_t pumpingDirection);
void infuseVolume();
void infuseTime();
void refillVolume();
void refillFull();
void pumpSingly(int8_t pumpingDirection, uint32_t flowrate, uint32_t volume);
void pumpContinuously();
uint8_t pump(uint32_t flowrate, uint32_t volume);



/********************************************************************
  setup
********************************************************************/
void setup()
{
  lcd.begin(16, 2);

  pinMode(STEP_PIN, OUTPUT);
  pinMode(DIRECTION_PIN, OUTPUT);
  pinMode(ENABLE_PIN, OUTPUT);
  pinMode(ENDSTOP_PIN1, INPUT_PULLUP);
  pinMode(ENDSTOP_PIN2, INPUT_PULLUP);
  pinMode(BUZZER_PIN, OUTPUT);

  digitalWrite(ENABLE_PIN, HIGH);

  items[1]  = {5, 0, 2, 0, TEXT, "Infuse"};
  items[2]  = {7, 1, 3, 0, TEXT, "Refill"};
  items[3]  = {9, 2, 4, 0, TEXT, "Cycle Mode"};
  items[4]  = {10, 3, 0, 0, TEXT, "Settings"};
  items[5]  = {15, 0, 6, 1, TEXT, "Target Volume"};
  items[6]  = {16, 5, 0, 1, TEXT, "Target Time"};
  items[7]  = {17, 0, 8, 2, TEXT, "Full Refill"};
  items[8]  = {18, 7, 0, 2, TEXT, "Target Volume"};
  items[9]  = {19, 0, CHANGEVALUE, 3, FLOWRATE, "infuse flow:", 1, 120000000};
  items[10] = {20, 0, 11, 4, TEXT, "Units"};
  items[11] = {23, 10, 12, 4, TEXT, "Syringe"};
  items[12] = {25, 11, 13, 4, LIST, "Sound", 2};
  items[13] = {27, 12, 14, 4, LIST, "EEPROM", 3};
  items[14] = {FIRMWAREINFO, 13, 0, 4, TEXT, "Firmware"};
  items[15] = {29, 0, CHANGEVALUE, 5, VOLUME, "volume:", 4, 1000000};
  items[16] = {30, 0, CHANGEVALUE, 6, TIME, "time:", 5, 60000};
  items[17] = {REFILLFULL, 0, CHANGEVALUE, 7, FLOWRATE, "flowrate:", 6, 2000000};
  items[18] = {31, 0, CHANGEVALUE, 8, VOLUME, "volume:", 7, 1000000};
  items[19] = {CYCLEMODE, 0, CHANGEVALUE, 9, FLOWRATE, "refill flow:", 8, 2000000};
  items[20] = {32, 0, 21, 10, LIST, "Volume Units", 9};
  items[21] = {34, 20, 22, 10, LIST, "Time Units", 10};
  items[22] = {37, 21, 0, 10, LIST, "Flowrate Units", 11};
  items[23] = {41, 0, 24, 11, TEXT, "Diameter"};
  items[24] = {42, 23, 0, 11, TEXT, "Length/Volume"};
  items[25] = {SELECTFROMLIST, 0, 26, 12, TEXT, "on"};
  items[26] = {SELECTFROMLIST, 25, 0, 12, TEXT, "off"};
  items[27] = {SELECTFROMLIST, 0, 28, 13, TEXT, "on"};
  items[28] = {SELECTFROMLIST, 27, 0, 13, TEXT, "off"};
  items[29] = {INFUSEVOLUME, 0, CHANGEVALUE, 15, FLOWRATE, "flowrate:", 12, 2000000};
  items[30] = {INFUSETIME, 0, CHANGEVALUE, 16, FLOWRATE, "flowrate:", 13, 2000000};
  items[31] = {REFILLVOLUME, 0, CHANGEVALUE, 18, FLOWRATE, "flowrate:", 14, 2000000};
  items[32] = {SELECTFROMLIST, 0, 33, 20, TEXT, "mL"};
  items[33] = {SELECTFROMLIST, 32, 0, 20, TEXT, "uL"};
  items[34] = {SELECTFROMLIST, 0, 35, 21, TEXT, "s"};
  items[35] = {SELECTFROMLIST, 34, 36, 21, TEXT, "min"};
  items[36] = {SELECTFROMLIST, 35, 0, 21, TEXT, "h"};
  items[37] = {SELECTFROMLIST, 0, 38, 22, TEXT, "mL/s"};
  items[38] = {SELECTFROMLIST, 37, 39, 22, TEXT, "mL/min"};
  items[39] = {SELECTFROMLIST, 38, 40, 22, TEXT, "uL/s"};
  items[40] = {SELECTFROMLIST, 39, 0, 22, TEXT, "uL/min"};
  items[41] = {0, 0, CHANGEVALUE, 23, DIAMETER, "diameter:", 15, 11284};
  items[42] = {0, 0, CHANGEVALUE, 24, LENGTHPERVOLUME, "length/volume:", 16, 10000};

  for (uint8_t i = 1; i < NITEMS; i++)
  {
    if (items[i].type != TEXT) readFromEEPROM(i);
  }

  recalculateSyringe(LINK2DIA);
  beep();
  showScreensaver();
}



/********************************************************************
  loop
********************************************************************/
void loop()
{
  uint8_t nextItem;
  getButtonState();
  if (buttonState == SHORTPRESS && lastButton != SELECT)
  {
    buttonState = MEDIUMPRESS;

    nextItem = items[currentItem].button[lastButton];
    if (nextItem != 0 && nextItem < 200)
    {
      currentItem = nextItem;
      printScreen();
    }
    else if (nextItem == CHANGEVALUE) changeValue();
    else if (nextItem == SELECTFROMLIST) selectFromList();
    else if (nextItem == INFUSEVOLUME) infuseVolume();
    else if (nextItem == INFUSETIME) infuseTime();
    else if (nextItem == REFILLVOLUME) refillVolume();
    else if (nextItem == REFILLFULL) refillFull();
    else if (nextItem == CYCLEMODE) pumpContinuously();
    else if (nextItem == FIRMWAREINFO) printFirmwareInfo();
  }
}



/********************************************************************
  getValue
********************************************************************/
uint32_t getValue(uint8_t itemNo)
{
  uint16_t divider = valueDivider(items[itemNo].type);
  uint8_t lastDigitIncrement = 0;
  if ( uint16_t(items[itemNo].value % divider) > divider / 2) lastDigitIncrement = 1;

  if (items[itemNo].value / divider > 99999999)
  {
    items[itemNo].value = divider * 99999999;
    return 99999999;
  }
  else return (items[itemNo].value / divider) + lastDigitIncrement;
}



/********************************************************************
  changeValue
********************************************************************/
void changeValue()
{
  uint8_t digits[8];
  uint32_t value = getValue(currentItem);
  for (int8_t i = 7; i >= 0; i--)
  {
    digits[i] = uint8_t(value % 10);
    value /= 10;
  }

  lcd.setCursor(0, 1);
  for (int8_t i = 0; i < 4; i++) lcd.print(digits[i]);

  lcd.setCursor(0, 1);
  lcd.cursor();
  int8_t i = 0;
  while (i >= 0 && i < 8)
  {
    getButtonState();
    if (buttonState == SHORTPRESS || buttonState == LONGPRESS)
    {
      if (lastButton == UP) digits[i] = (digits[i] + 1) % 10;
      else if (lastButton == DOWN) digits[i] = (digits[i] + 9) % 10;
      lcd.print(digits[i]);

      if (lastButton == RIGHT) i++;
      else if (lastButton == LEFT) i--;

      if (i == -1 && buttonState != SHORTPRESS) i++;
      if (i == 8 && buttonState != SHORTPRESS) i--;

      if (i < 5)lcd.setCursor(i, 1);
      else lcd.setCursor(i + 1, 1);

      if (buttonState == SHORTPRESS) buttonState = MEDIUMPRESS;
      else if (buttonState == LONGPRESS)
      {
        uint32_t nextMillis = millis() + AUTOCHANGINGDELAY;
        while (nextMillis > millis() && buttonState == LONGPRESS) getButtonState();
      }
    }
  }

  if (i == 8)
  {
    bool isSame = true;
    value = getValue(currentItem);
    for (int8_t j = 7; j >= 0 && isSame == true; j--)
    {
      if (digits[j] != uint8_t(value % 10)) isSame = false;
      value /= 10;
    }

    bool isZero = true;
    for (int8_t j = 7; j >= 0 && isZero == true; j--)
    {
      if (digits[j] != 0) isZero = false;
    }

    if (isSame == false && isZero == false)
    {
      setValue(currentItem, digits);
      beep();
    }
  }

  lcd.noCursor();
  lcd.setCursor(0, 1);
  printScreen();
}



/********************************************************************
  setValue
********************************************************************/
void setValue(uint8_t itemNo, uint8_t digits[8])
{
  uint32_t value = 0;
  for (int8_t i = 0; i < 8; i++) value = value * 10 + digits[i];

  uint16_t divider = valueDivider(items[itemNo].type);
  if (4294000000 / divider < value) items[itemNo].value = 4294000000;
  else items[itemNo].value = value * divider;

  if (itemNo == LINK2LPV || itemNo == LINK2DIA)
  {
    recalculateSyringe(itemNo);
    writeToEEPROM(LINK2LPV);
    writeToEEPROM(LINK2DIA);
  }
  else writeToEEPROM(itemNo);
}



/********************************************************************
  selectFromList
********************************************************************/
void selectFromList()
{
  uint8_t parentItem = items[currentItem].button[LEFT];
  items[parentItem].button[RIGHT] = currentItem;
  writeToEEPROM(parentItem);
  beep();
  currentItem = parentItem;
  printScreen();
}



/********************************************************************
  calculateActualValue
********************************************************************/
void calculateActualValue(uint8_t itemNo)
{
  if (items[itemNo].type == FLOWRATE)
  {
    float maxFlowrate = 1e9 * MAXRPM * MMPER360 / (float)items[LINK2LPV].value;
    if ((float)(items[itemNo].value) > maxFlowrate) items[itemNo].value = (uint32_t)maxFlowrate;

    float ustepsPERmin = coef * NOFMICROSTEPS * (float)items[itemNo].value;
    if (ustepsPERmin < 14.4) ustepsPERmin = 14.4;
    float multiplier;
    if (ustepsPERmin >= 229) multiplier = 15000000;
    else multiplier = 937500;
    float tempFloat = multiplier / ustepsPERmin;
    uint16_t countsPERustepActual = (uint16_t)(tempFloat + 0.5);
    tempFloat = multiplier / (float)countsPERustepActual;
    tempFloat /= (float)(coef * NOFMICROSTEPS);
    items[itemNo].value = (uint32_t)tempFloat;
  }

  else if (items[itemNo].type == VOLUME)
  {
    uint32_t nSteps = (uint32_t)(coef * (float)items[itemNo].value + 0.5);
    float tempFloat = (float)nSteps / coef;
    items[itemNo].value = (uint32_t)tempFloat;
  }

  else if (items[itemNo].type == TIME)
  {
    if (items[itemNo].value > 59994000) items[itemNo].value = 59994000;
    items[itemNo].value -= (items[itemNo].value % 1000);
  }
}
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

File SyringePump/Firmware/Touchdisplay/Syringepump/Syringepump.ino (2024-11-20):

#include <Arduino.h>
#include <lvgl.h>
#include "display.h"
#include "esp_bsp.h"
#include "lv_port.h"

#include "ui.h"


#include <ESP_FlexyStepper.h>



// create the stepper motor object
ESP_FlexyStepper stepper;

int previousDirection = 1;

//variables for software debouncing of the limit switches
unsigned long lastDebounceTime = 0;
unsigned long debounceDelay = 100; //the minimum delay in milliseconds to check for bouncing of the switch. Increase this slighlty if you switches tend to bounce a lot
bool buttonStateChangeDetected = false;
byte limitSwitchState = 0;
byte oldConfirmedLimitSwitchState = 0;

  const int MOTOR_STEP_PIN      = 5;    //  1
  const int MOTOR_DIRECTION_PIN = 6;    //  2
  const int MOTOR_EN_PIN        = 7;    //  3
  const int LIMIT_SWITCH_PIN    = 15;   //  4 // using internal Pullup and in series with NC (Normally Closed) mode


// Speed settings
const int DISTANCE_TO_TRAVEL_IN_STEPS = 2000;
const int SPEED_IN_STEPS_PER_SECOND = 300;
const int ACCELERATION_IN_STEPS_PER_SECOND = 800;
const int DECELERATION_IN_STEPS_PER_SECOND = 800;



static int variable = 0; // Variable to be controlled by slider and buttons
static lv_obj_t * label_variable; // Label to display variable value


// Event handler for slider
static void slider_event_handler(lv_event_t * e)
{
    lv_obj_t * slider = lv_event_get_target(e);
    variable = lv_slider_get_value(slider);
    // Place your code here to handle the variable change by slider
    printf("Slider value changed: %d\n", variable);
    lv_label_set_text_fmt(label_variable, "Value: %d", variable); // Update label with new value

}

// Event handler for buttons
static void button_event_handler(lv_event_t * e)
{
    lv_obj_t * button = lv_event_get_target(e);
    const char * label = lv_label_get_text(lv_obj_get_child(button, 0));
    
    if (strcmp(label, "STEP+") == 0) {
        variable++;
    } else if (strcmp(label, "STEP-") == 0) {
        variable--;
    } else if (strcmp(label, "START") == 0) {
        // Place your code here to handle the start action
        printf("Start button pressed\n");
    } else if (strcmp(label, "STOP") == 0) {
        // Place your code here to handle the stop action
        printf("Stop button pressed\n");
    } else if (strcmp(label, "HOME") == 0) {
        // Place your code here to handle the homing action
        printf("Home button pressed\n");
    }
    
    // Place your code here to handle the variable change by buttons
    printf("Button pressed, new value: %d\n", variable);
}
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

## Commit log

2024-11-17 initial Upload to Git
    [ControllerPiggyback-Körper001.3mf, ControllerPiggyback.FCStd, OrbitalShaker_all.3mf, PlatformSupport_NEW-support platform.step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]
2024-11-20 Created obj. for Maya workshop
    [PotiTower-Körper.obj, Shaker_Case.obj, Unbenannt1-Shaker_CaseTop.obj, Unbenannt3-NewPlatform.obj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]
